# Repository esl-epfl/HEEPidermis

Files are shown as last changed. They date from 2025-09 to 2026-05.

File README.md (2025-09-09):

# Welcome!

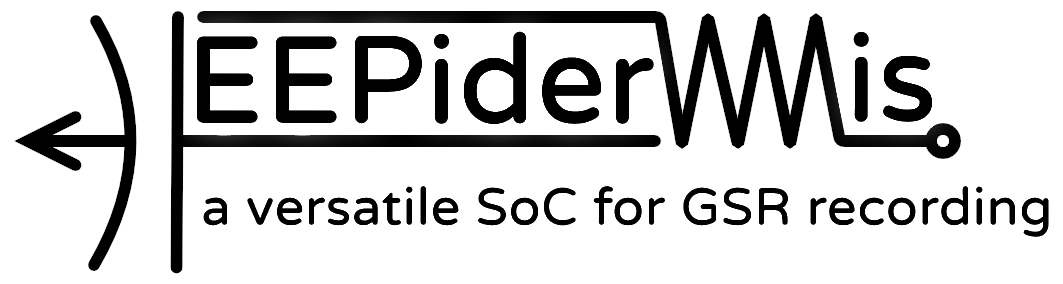
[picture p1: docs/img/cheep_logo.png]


HEEPidermis is a chip based on the open-source RISC-V platform [X-HEEP](https://github.com/esl-epfl/x-heep) intended to record Galvanic Skin Response (GSR) and Impedance (Z).
HEEPidermis is capable of injecting arbitrary-wave currents on the skin with an 8-bit iDAC and measure voltage through a 14-bit VCO-based ADC.
Parameters of the iDAC and ADC can be programmed dynamically using the on-board Ibex CPU. Acquired data can be stored in the 16 kB RAM memory for on-chip processing, compression, and transmission.

HEEPidermis can be interfaced through JTAG for code-debugging, SPI to obtain recordings from memory, or UART.
External ADCs and peripherals can also be commanded via SPI.

The Direct Memory Access (DMA) block allows the chip to operate autonomously without the constant interaction of the CPU. Given proper configuration, the DMA can take care of controlling the current injection profile, read data from the local ADC (or an external one), store data and/or transmit it through SPI.
The DMA can additionally re-direct data to a digital Level Crossing (dLC) block to filter data and reduce the output data rate. The output of the dLC can be stored in memory (along timestamps) or be exposed to be used as feedback loop for the analog front-end, interface with transmission circuits or as input to Spiking Neural Networks.
The dLC block also accepts inputs from analog LC ADCs (instead of the on-chip ADC).

HEEPidermis can also decimate 1-bit ΔΣ-ADCs' output with an integrated CIC filter or, alternatively, with an integrated custom smoothing stage, followed by the dLC block.

Being based on the X-HEEP platform, you can check its documentation on how to program, debug, or understand how it was built. We suggest using the [vendorized X-HEEP's documentation](../../hw/vendor/x-heep/docs/source/index.rst).
For all HEEPidermis-specific documentation, please refer to the documentation below.



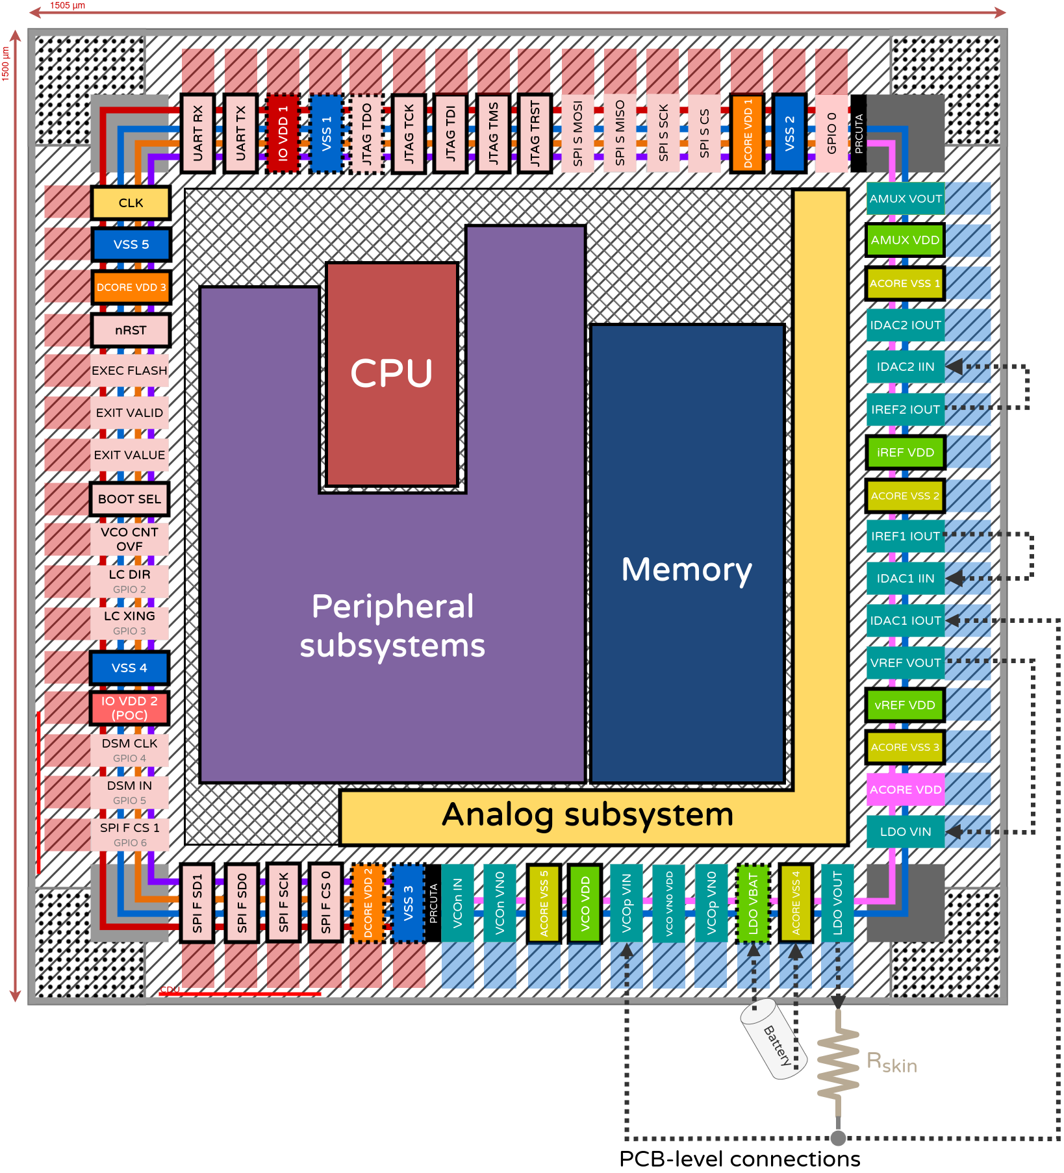
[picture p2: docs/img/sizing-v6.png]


## Index

- **Analog Front End**
  - [Analog subsystem](hw/ip/analog_subsystem/README.md)
  - [iDAC](hw/vendor/analog-library/iDAC/docs/README.md)
  - [VCO](hw/vendor/analog-library/VCO/docs/README.md)

- **Digital Back End**
  - [CPU](./docs/source/DBE/CPU.md)
  - [DMA (how we use it)](./docs/source/DBE/DMA.md)
  - [DMA](hw/vendor/x-heep/docs/source/Peripherals/DMA.md)
  - [SPI host](hw/vendor/x-heep/docs/source/Peripherals/SPI.md)
  - [SPI slave](hw/vendor/x-heep/docs/source/Peripherals/SPI_slave.md)
  - [digital Level-Crossing](hw/vendor/x-heep/docs/source/ExternalPeripherals/dLC.md)
  - [ΔΣ decimation (CIC filter)](./docs/source/DBE/CIC_filter.md)
  - [ΔΣ decimation (SES filter)](./docs/source/DBE/SES_filter.md)

- **Related documents**
  - [HEEPidermis](https://arxiv.org/abs/2509.04528)
  - [ΔΣ Decimation theory](https://ieeexplore.ieee.org/abstract/document/11044062)
  - [iDAC precursor](https://ieeexplore.ieee.org/document/11044212)
  - [VCO Design](https://arxiv.org/abs/2509.06698)

## Prerequisites

Since this project is based on _X-HEEP_, it has the same prerequisites.

1. Follow _X-HEEP_'s [_Prerequisite_](https://github.com/esl-epfl/x-heep/tree/main#prerequisite) section to download the necessary tools.
To correctly generate hardware and software, an extended version of the _core-v-mini-mcu_ environment is required. To install it run:
   ```Bash
   make conda
   ```
Make sure the Conda environment is active:
   ```Bash
   conda activate heepidermis
   ```

2. Make sure that the following tools are available in your system's `PATH`:
   - RISC-V toolchain (supporting at least `rv32imc`)
   - Verible
   - GTKWave
   - Siemens QuestaSim version 2020.4 or above
   - Synopsys Design Compiler version 2020.09 or above
   - Verilator 4

### RTL Simulation

The included [`makefile`](./makefile) proves all the necessary rules to build _HEEPidermis_:

1. Generate all the RTL files (and software headers):
   ```bash
   make cheep-gen
   ```
   Some _X-HEEP_ configuration parameters (e.g. `BUS`, `MEMORY_BANKS` etc.) are still supported, although the default configuration may differ (check [`peripherals_config`](./config/peripherals_config)). In general, these should not be passed through the makefile targets but should be configured in the hjson files in the `config` folder.

2. Build the simulation model:
   ```bash
   make verilator-build     # Verilator
   make questasim-build     # QuestaSim
   ```

3. The software build process is primarily handled by _X-HEEP_, and most of its [example applications](./hw/vendor/x-heep/sw/applications/) will work on _HEEPidermis_ as well. You can choose other `BOOT_MODE`, just be sure to match it with the one used with `make *-build` (by default they use `fore`). `force` will be the faster for simulation.

```bash
make app PROJECT=test_dlc_vco BOOT_MODE=force
```

The combinations of compatible linker and boot modes can be found here:
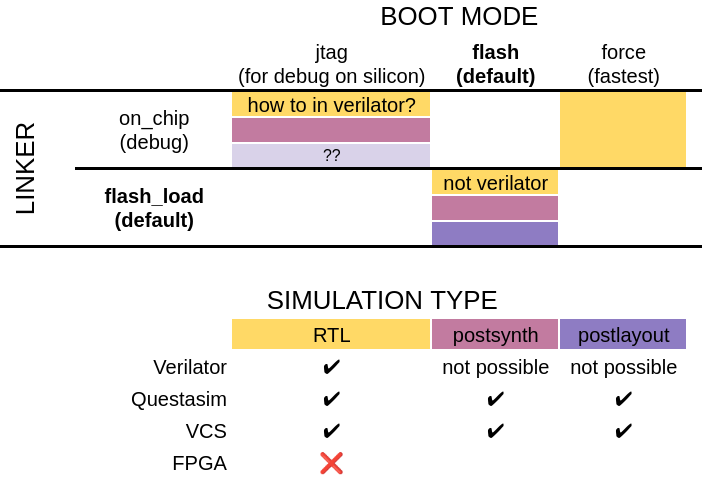
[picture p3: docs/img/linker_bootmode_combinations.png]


1. Launch the simulation with the compiled firmware:
   ```bash
   make verilator-run       # Verilator with waveforms dump
   make verilator-opt       # Verilator without waveforms dump
   make questasim-run       # QuestaSim
   make questasim-gui       # QuestaSim with GUI
   ```

   You can also set other parameters like the `FUSESOC_FLAGS`, `LOG_LEVEL`, `BOOT_MODE`, `VCD_MODE`, etc. to customize the simulation. Refer to the [`makefile`](./makefile) for more details.

2. _HEEPidermis_ `stdout` is exposed through a UART DPI interface at `/dev/pts/<N>`, where `N` is a number printed on the simulation log during execution. You can connect to it using `screen` or similar tools, e.g.:
   ```bash
   screen /dev/pts/0
   ```
   The UART output is also stored to the `uart.log` file in the common simulation directory (`build/sim-common/uart.log`).
   > Using `printf()` will significantly increase the firmware execution time and therefore the simulation. For quick debugging, it recommended to use the return value from `main` instead. When it is _not_ zero, the testbench will print it out at the end of the simulation.

3. The waveforms dumped during the simulation can be opened using:
   ```bash
   make verilator-waves # after Verilator simulation
   make questasim-waves # after QuestaSim simulation
   ```

This will open the waveforms (example from `test_dlc_vco` application):
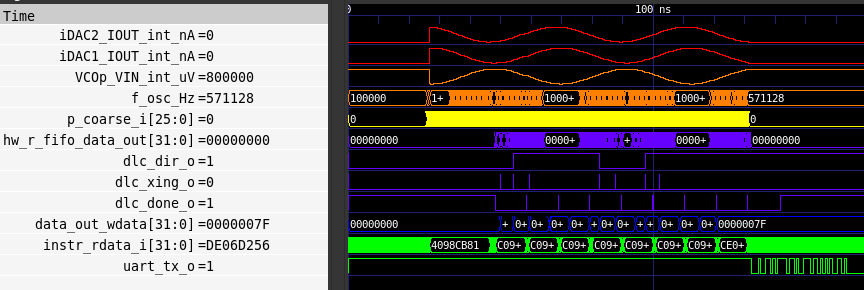
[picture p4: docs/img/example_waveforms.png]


Assuming that your firmware is already available, steps 1., 3., and 4. can be repeated with a single command using the `verilator-sim` or `questasim-sim` targets.

# Questions?

Have questions? curiosities? ideas on how to exploit HEEPidermis? Want to contribute on following versions of the SoC?
Drop an email :) juan.sapriza@epfl.ch

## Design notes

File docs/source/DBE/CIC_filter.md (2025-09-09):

# CIC filter

The CIC filter is implemented as a simplified version of the existing `PDM2PCM` block in the X-HEEP platform. This is achieved by adding a configuration flag, `cic_only`, in the `mcu_cfg.hjson` file. During the `mcu-gen` process, this flag instructs the Python generation scripts to output a reduced SystemVerilog implementation tailored for CIC-only operation, using Mako templates.

For clarity and conciseness, the remainder of this section focuses exclusively on the reduced CIC-only configuration of the block, highlighting the specific modifications made to the original `pdm2pcm` implementation. Additionally, topics shared with the SES filter are covered in greater detail in the corresponding SES section.

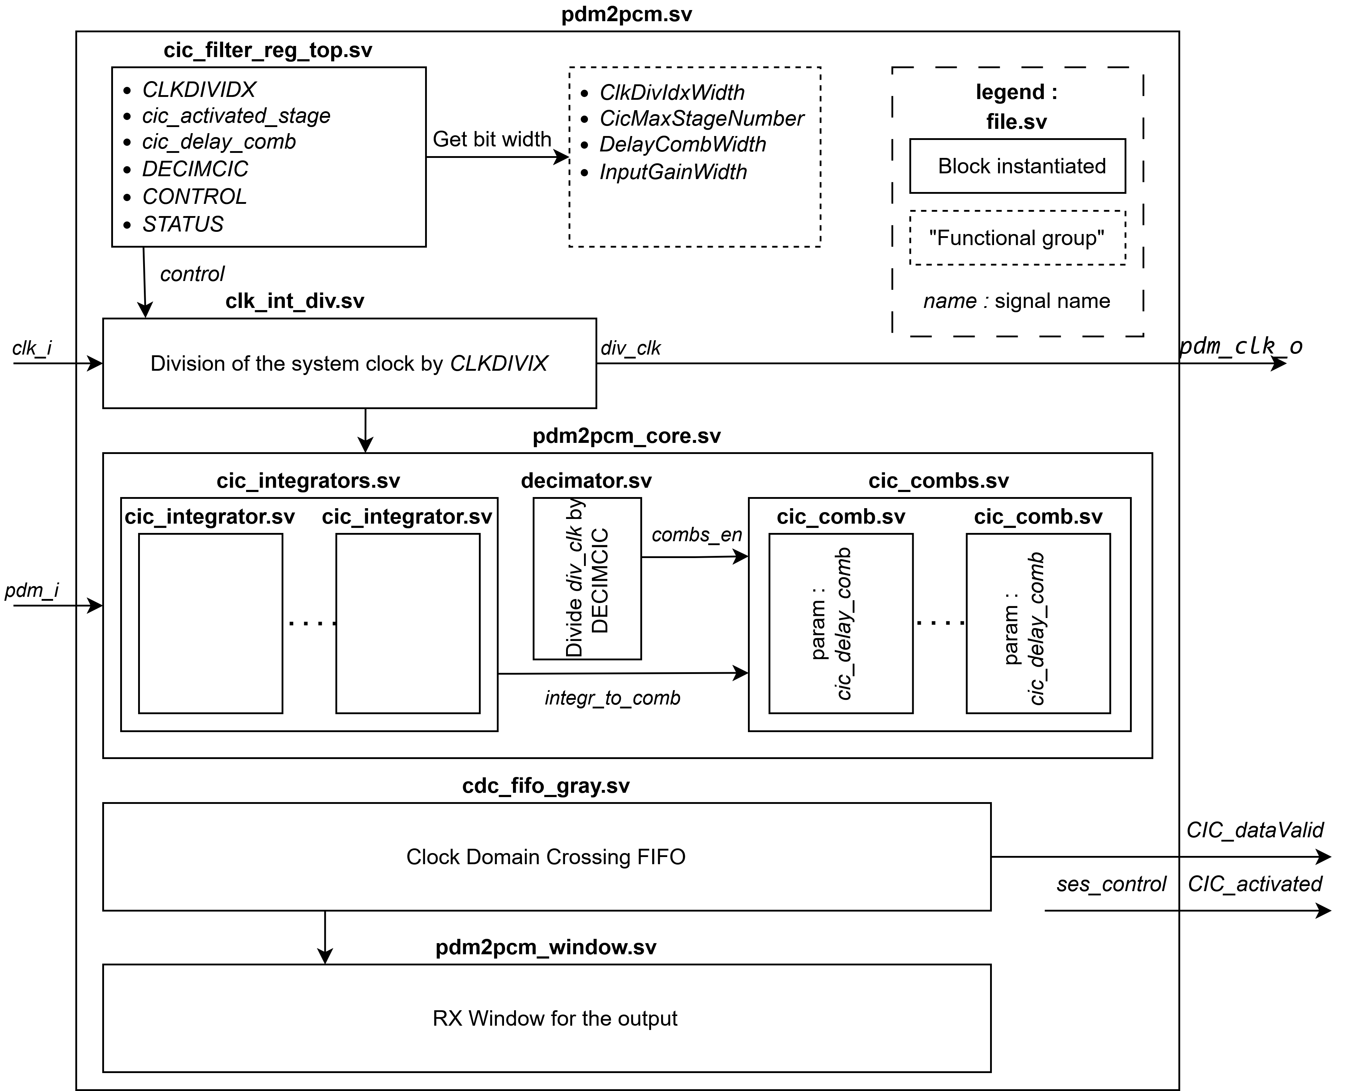
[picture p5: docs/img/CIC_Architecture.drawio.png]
Top level system verilog architecture representation

*Figure: Top level system verilog architecture representation*

## Runtime configurability

This implementation utilizes X-HEEP’s register abstraction to enable seamless communication between C code and SystemVerilog, as detailed in Section SES filter. In the case of the CIC filter, the relevant memory-mapped registers are defined in `pdm2pcm.hjson`.

The following registers are used in the CIC filter configuration:

- **CONTROL** (2 bits): Software control register. The LSB enables or disables the filter; the MSB clears the FIFO buffer.
- **STATUS** (2 bits): Indicates filter status. The LSB signals whether the FIFO is empty, while the MSB indicates if it is full.
- **DECIMCIC** (4 bits): Sets the decimation factor applied between the sampling frequency and the output rate.
- **CLKDIVIDX** (16 bits): Configures the divider between the system clock and the sampling clock.
- **cic_activated_stages** (6 bits): Thermometric, right-aligned bitmask specifying the active CIC stages. The 1s must be contiguous.
- **cic_delay_comb** (4 bits): Defines the delay parameter \( D \) used in the comb stage.
- **RXDATA** (32 bits): Provides access to the filtered output data through a memory-mapped FIFO window.

Detailed information regarding access permissions and bitfield definitions can be found directly in the corresponding `.hjson` configuration file.

## Automatic width adaptation

As for the SES filter, the CIC was updated to allow configuration directly from the width of the register. See more in the corresponding section.

## Integrators and combs

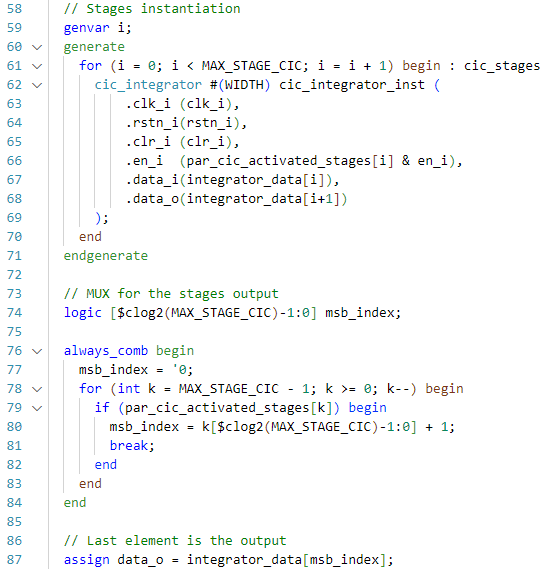
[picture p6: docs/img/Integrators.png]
integrators.sv code snippet, showing the output MUX'ing and the stage generation


*Figure: integrators.sv code snippet, showing the output MUX'ing and the stage generation*

The files `integrators.sv` and `combs.sv` define their respective sections of the CIC filter as parameterized generate blocks. A configurable number of stages is instantiated based on the design parameter `MAX_STAGE_CIC`, with each stage connected in series. This parameter is determined at compile time by checking the width of the `par_cic_activated_stages` register. Stage activation is controlled by the thermometric input `par_cic_activated_stages`, allowing runtime flexibility.

A small combinational logic block scans this activation mask to determine the highest active stage and selects its output for `data_o`. This enables dynamic configuration of the filter depth while maintaining a compact and hardware-efficient implementation.

## Delay D in comb

This block implements a single-stage comb filter, which forms part of the CIC decimation chain. The parameter `par_delay` defines the delay D used in the comb difference equation. Depending on the value of `par_delay`, the filter either bypasses subtraction (when delay is 0) or computes the difference between the current input `data_i` and a delayed version stored in `r_previousdata[par_delay - 1]`.

To support runtime selection of the delay, a shift register of size `MAX_DELAY` stores recent input samples. On each clock cycle (when `en_i` is asserted), the new input is inserted at index 0, and all previous values are shifted forward. This allows the output difference to be computed with any delay value up to `MAX_DELAY`, providing runtime flexibility while maintaining hardware simplicity.

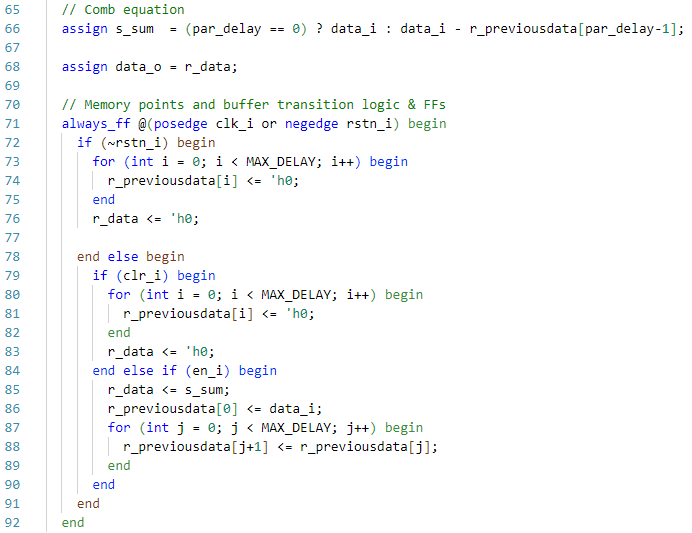
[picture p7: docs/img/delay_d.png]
comb.sv code snippet, showing the usage of the delay parameter

*Figure: comb.sv code snippet, showing the usage of the delay parameter*

## Results

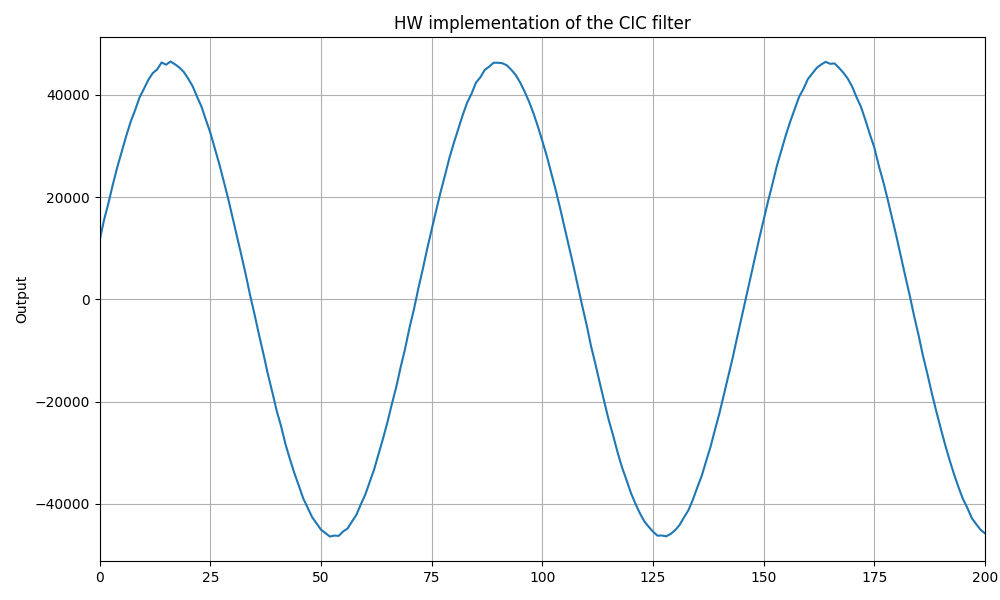
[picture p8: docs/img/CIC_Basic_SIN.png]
Proof of concept, using a perfect sinusoid as input

*Figure: Proof of concept, using a perfect sinusoid as input*

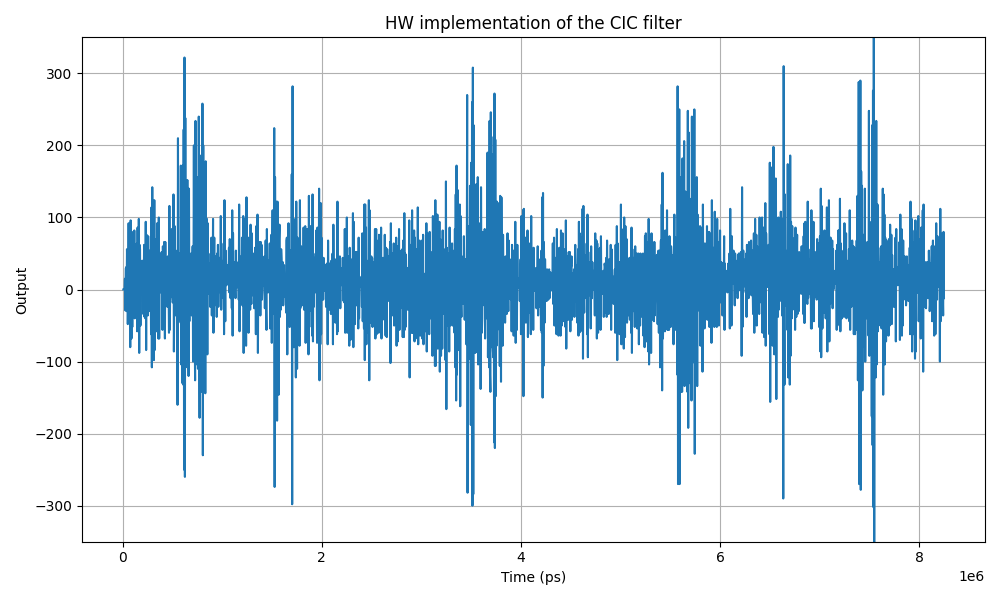
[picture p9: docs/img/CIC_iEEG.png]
Hardware output of the iEEG_10000Hz_85OSR_65dBFS sample file

*Figure: Hardware output of the iEEG_10000Hz_85OSR_65dBFS sample file*

The results obtained for the sinusoidal input closely match the expected ground truth, demonstrating correct filter behavior. Additionally, the output for real EEG signals appears clean and free of significant artifacts. These observations support the successful validation of the project objective.

## Usage

An example of the filter's usage from the software side is provided in the `example_cic` project. This program validates the functionality of the CIC block by comparing its output against predetermined ground truth values.

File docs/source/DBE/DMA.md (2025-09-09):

#  DMA

We have 2 DMA channels. Each DMA channel has an explicit purpose: 

1) For the ADC - to read data from the VCO-ADC decoder
2) For the iDAC - to write data to the iDAC controller

Two DMA channels are needed in order to perform transactions in parallel (injecting current and reading at the same time). 

## The ADC DMA

The ADC DMA should make a reading from the VCO decoder `value` register shortly after the reading value is ready. For this, we have included a dedicated [ADC-timer](./Timers.md) instantiated on the external peripheral subsystem. In SW the timer should be set to the sampling frequency of the ADC. When the timer count has finished it will trigger a refresh signal in the ADC decoder. This will propagate first to the VCO-ADC to get a sample, and few clock cycles later to an `vco_data_ready` signal that is used as a trigger for the DMA through `ext_dma_slot_rx[0]`. This slot enables the DMA to perform one data movement, from the source target (the decoder's `value` register) to a pre-configured destination. 

The ADC DMA is additionally connected to a **streaming accelerator: [the dLC block](./dLC.md)** on the HW-FIFO interface. It can be configured to pass the data through the dLC. This filters the data (decides if and what should be stored) and can proceed to store the resulting value instead of the original one obtained from the VCO-ADC.    

## The DAC DMA

The DAC DMA is used to write into the iDAC registers (primarly the `value` register). To perform this operation at the iDACs refresh-rate, the trigger is controlled by a dedicated [DAC-timer](./Timers.md) also on the external peripheral subsystem. 

## Alternative use: dual-channel VCO + DC current. 

In the case of using DC current, the DAC-DMA will be free, so it could be used to control a second VCO-ADC. 

> ⚠️⚠️⚠️ @ToDo: HOW???!!

## Alternative use: Double-tap operation of the VCO-ADC

If the sampling frequency for the ADC is too slow the counter that keeps track of the number of oscillations will overflow. One alternative to make readings in this case is to do a double-tap: Making a measurement, waiting a short period of time (at some point we had done the math and it was ~300 µs) and perform another reading. 

> ⚠️⚠️⚠️ @ToDo: HOW???!!

## Controlling it from software

The DMAs are completely compatible with the X-HEEP DMA, so please refer to its [documentation](https://x-heep.readthedocs.io/en/latest/Peripherals/DMA.html#) and [examples](https://github.com/esl-epfl/x-heep/tree/main/sw/applications/example_dma) for use cases. 

Below is basic use case configuring the DAC-DMA to write into the iDAC and the ADC-DMA to read the resulting values from the VCO-ADC. 

<details>
<summary>Example code to configure the DMAs</summary>

🎵 Never gonna give you up... 🎶  👀

</details>

## Questions? 

| Topic | Responsible |
|---------------|---------------|
| Mutlichannel | Tommaso Terzano |
| Reconfigurability | Tommaso Terzano |
| HW FIFO | Alessio Naclerio |
| Software | Juan Sapriza, Tommaso Terzano |
| General | Juan Sapriza, Tommaso Terzano, Davide Schiavone |

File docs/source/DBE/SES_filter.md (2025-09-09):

## SES Filter

### Introduction

The filter implemented is a variant of Brown’s Simple Exponential Smoothing (SES) algorithm, adapted for low-power, hardware-efficient delta-sigma post-processing. Originally proposed by Sapriza et al., this SES filter provides a tunable and lightweight alternative to classical CIC filters, supporting runtime reconfiguration with minimal computational overhead.

In the context of *HEEPidermis*, the SES algorithm is expressed using shift-based arithmetic, making it highly suitable for hardware implementation without multipliers. The recursive formulation is as follows:

\[
    \begin{cases}
        \widehat{Y}_i = \widehat{Y}_{i-1} - \widehat{y}_{i-1} + \left(x_i \ll (W_g - 1)\right) \\
        \widehat{y}_i = \widehat{Y}_i \gg W_w
    \end{cases}
\]

Here, $\widehat{Y}_i$ represents the internal state (accumulator), $x_i$ is the 1-bit delta-sigma input scaled by $W_g$, and $W_w$ controls the smoothing strength. This structure enables tunable decimation and filtering with minimal resource usage, making it well-suited for ultra-low-power biomedical applications.

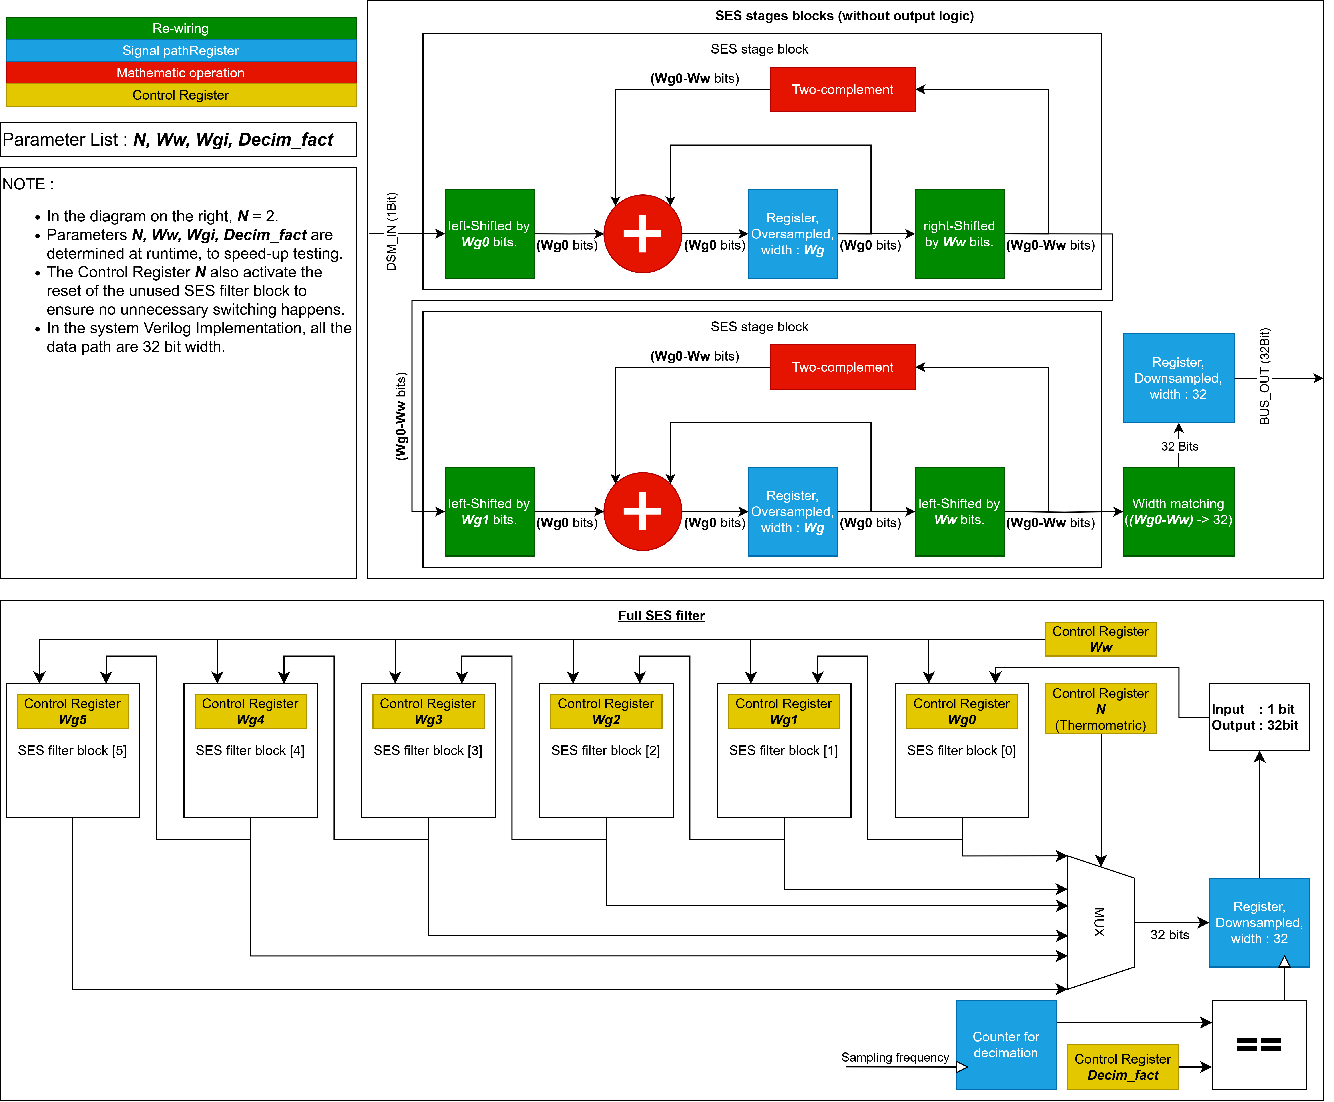
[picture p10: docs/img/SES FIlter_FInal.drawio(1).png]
Schematic representation of the SES filter architecture, showing individual processing stages and the output stage.

*Figure: Schematic representation of the SES filter architecture, showing individual processing stages and the output stage.*

---

### Setup

This setup assumes the installation from the Setup section was executed successfully. The following steps are based mostly on the README from the HEEPidermis GitLab repository.

If everything is set up correctly:

1. Fork the *HEEPidermis* repository to your personal GitLab account and clone it locally.
2. From the root directory of the cloned project, create the required Conda environment.

Once the environment is configured, the complete compilation and simulation flow is:

1. `make cheep-gen` — Generates the configured MCU architecture.
2. `make verilator-build` — Compiles the SystemVerilog sources and builds the simulation model using Verilator.
3. `make app PROJECT=myProject BOOT_MODE=force` — Compiles the C application specified by `myProject`.
4. `make verilator-run BOOT_MODE=force` — Runs the compiled application in the Verilator simulation environment.

---

### Implementation

#### Top level

The system is implemented in a newly created block with a top-level called `ses_filter.sv`. The general "software" architecture with the most important signals is shown below:

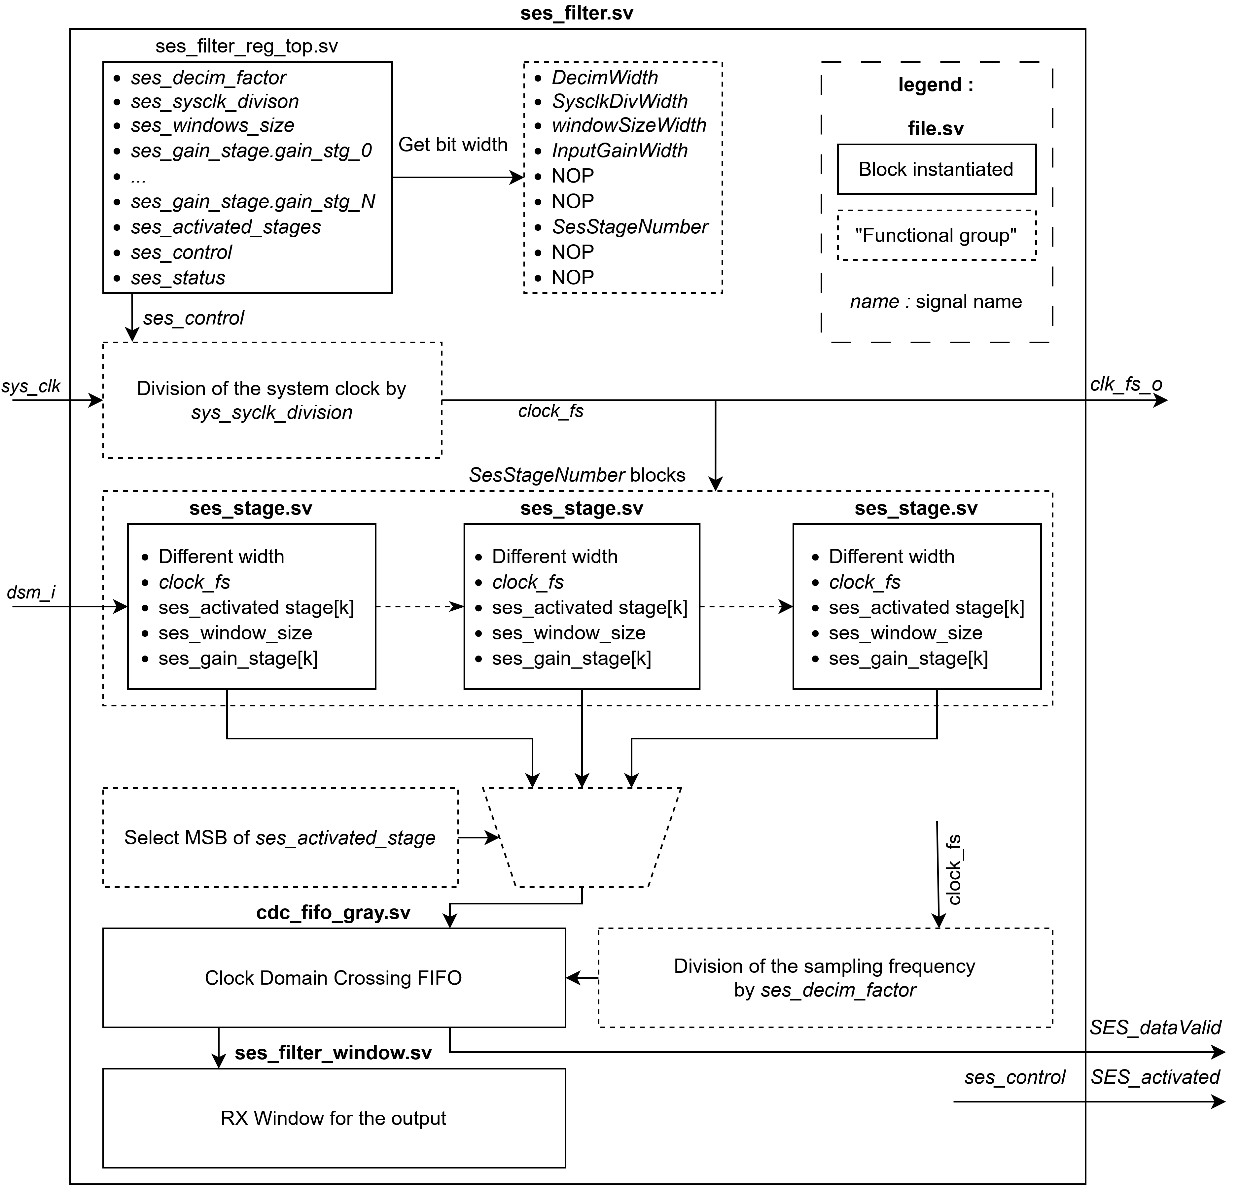
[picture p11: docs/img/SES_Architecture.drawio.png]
Top level system verilog architecture representation

*Figure: Top level system verilog architecture representation*

The design begins by downsampling the system clock to generate a lower-frequency sampling clock, referred to as `clock_fs`. This sampling clock drives the filter pipeline. To safely transfer data back to the system clock domain, a Clock Domain Crossing (CDC) FIFO is used.

A detailed description of the input and output ports is provided in the header comments of the `ses_filter.sv` file.

---

#### Runtime configurability

As for the CIC, this code leverages the X-HEEP/HEEPidermis platform's capability to interface between C code and SystemVerilog through a register abstraction mechanism. The registers are specified in the `ses_filter.hjson` file and generated using the `make cheep-gen` command, which calls the SES_filter.sh script and `regtool.py`.

The following memory-mapped registers are defined:

- **ses_control** (1 bit): Enables or disables the SES filter via software control.
- **ses_status** (2 bits): Provides filter status. LSB: filter active, MSB: new output data available.
- **ses_window_size** (5 bits): Sets the window size parameter \( W_w \) used in the filter computation.
- **ses_decim_factor** (10 bits): Defines the decimation factor applied between the sampling clock and the output rate.
- **ses_sysclk_division** (10 bits): Specifies the division factor from the system clock to the sampling clock.
- **ses_activated_stages** (6 bits): Thermometric, right-aligned bitmask indicating which SES stages are active. The 1s must be contiguous.
- **ses_gain_stages** (30 bits): Encodes the input gain \( W_{g,x} \) for each SES stage (5 bits per stage).
- **rx_data** (32 bits): FIFO window to retrieve filtered output data.

The files `ses_filter_reg_top.sv` and `ses_filter_reg_pkg.sv` are auto-generated and serve as the register interface. See the corresponding `.hjson` file for bitfield definitions.

---

#### Automatic width adaptation

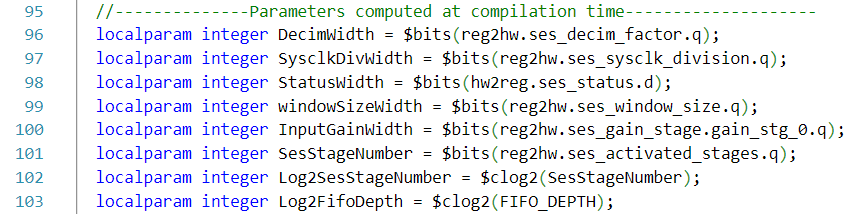
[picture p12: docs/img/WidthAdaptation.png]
ses_filter.sv code snippet, register width extraction

*Figure: ses_filter.sv code snippet, register width extraction*

This design maximizes flexibility by deriving most width-related and structural parameters directly from the register definitions. These values are resolved at compile time, allowing their use in generate blocks and signal width declarations.

For example, the maximum number of SES stages is computed from the width of the corresponding register field. Increasing the maximum number of SES stages only requires adjusting the width of the field and updating the gain configuration in the `.hjson` file. The SystemVerilog code adapts automatically.

The only parameters not derived from register fields are the datapath width (statically 32 bits) and the FIFO depth.

---

#### System clock decimation

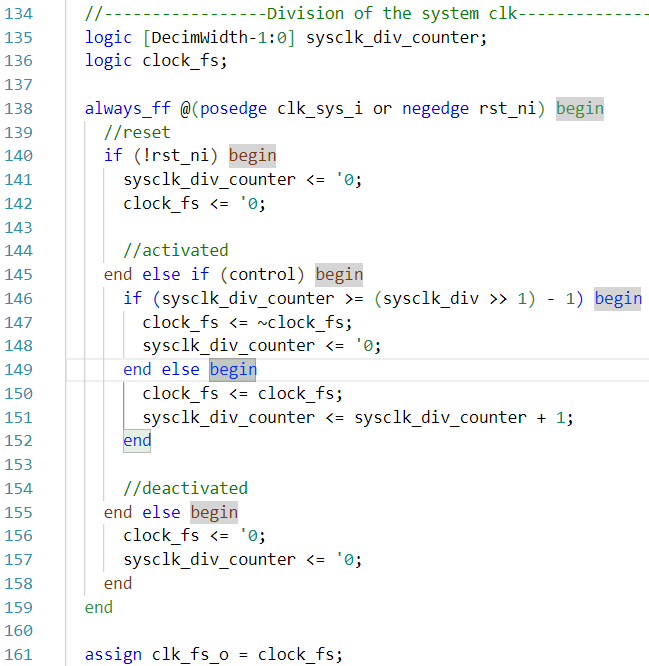
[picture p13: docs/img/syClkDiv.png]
ses_filter.sv code snippet, system clock decimation

*Figure: ses_filter.sv code snippet, system clock decimation*

This block implements a clock divider that generates the sampling clock signal, `clock_fs`, by dividing the main system clock `clk_sys_i` according to the value in `ses_sysclk_division`. The resulting clock `clock_fs` drives the SES filter and is output as `clk_fs_o` to trigger the connected recording device.

The divider logic includes enable and reset handling.

---

#### SES stage generation and internal logic

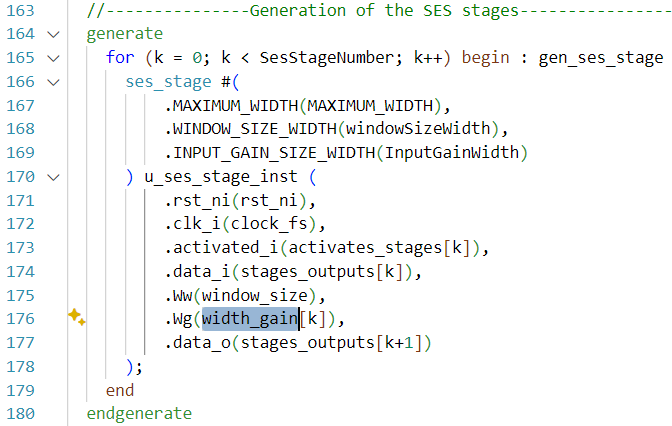
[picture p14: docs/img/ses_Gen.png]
ses_filter.sv code snippet, SES stage generation

*Figure: ses_filter.sv code snippet, SES stage generation*

The generate block instantiates the required number of SES stages based on the parameter derived from the register width. Each `ses_stage` instance is parameterized with maximum data width, window size width, and input gain width. Stages are connected sequentially, with output of stage `k` serving as the input to stage `k+1`. Stage activation and gain configuration are runtime configurable.

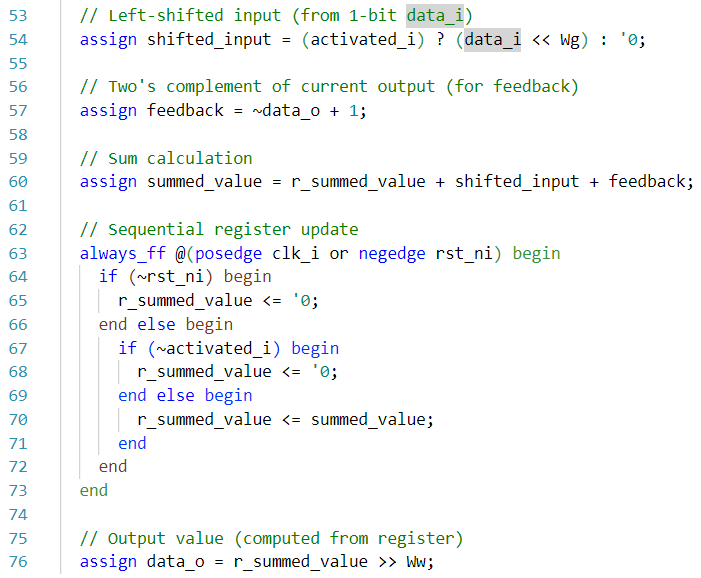
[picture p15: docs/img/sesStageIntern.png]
ses_stage.sv code snippet, internal logic of a single stage

*Figure: ses_stage.sv code snippet, internal logic of a single stage*

The internal logic of a single SES stage implements the mathematical formulation given above. The `activated_i` signal enables complete deactivation for energy-efficient operation.

The input bitstream `data_i` is left-shifted by the gain factor `Wg` when the stage is active. A feedback loop using two's complement implements the accumulator. The sum is stored in `r_summed_value`, reset upon deactivation or global reset. Output `data_o` is obtained by right-shifting the sum by `Ww`.

---

#### Output stage

The final stage is responsible for selecting the correct output, decimating the sampling frequency, and interfacing with the CDC FIFO.

1. **Output Selection (MUX):** The highest active SES stage is selected using a multiplexer.
2. **Decimation Counter:** A counter driven by the sampling clock reduces the output rate by the configured decimation factor.
3. **Clock Domain Crossing (CDC):** A dual-clock FIFO bridges the sampling and system clock domains, delivering data via the memory-mapped interface.
4. **Status Reporting:** A status register combines control state and FIFO validity for software monitoring.

---

## Results

For the following plots, filter parameters were as described in the behavioral model by Juan Sapriza.

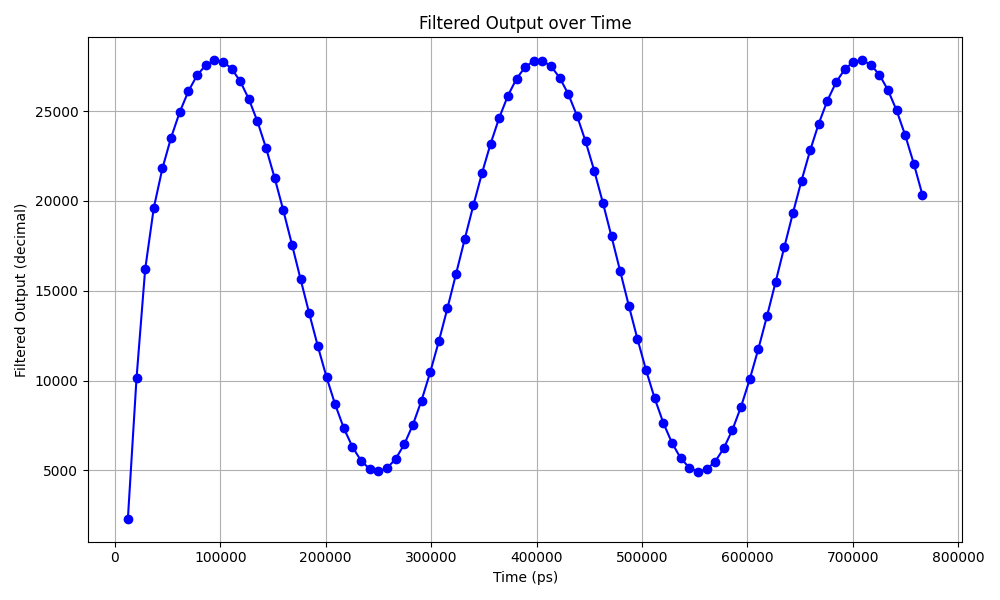
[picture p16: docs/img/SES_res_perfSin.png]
Proof of concept, using a perfect sinusoid as input

*Figure: Proof of concept, using a perfect sinusoid as input*

<div style="display: flex;">
  <div style="flex: 1; margin-right: 10px;">
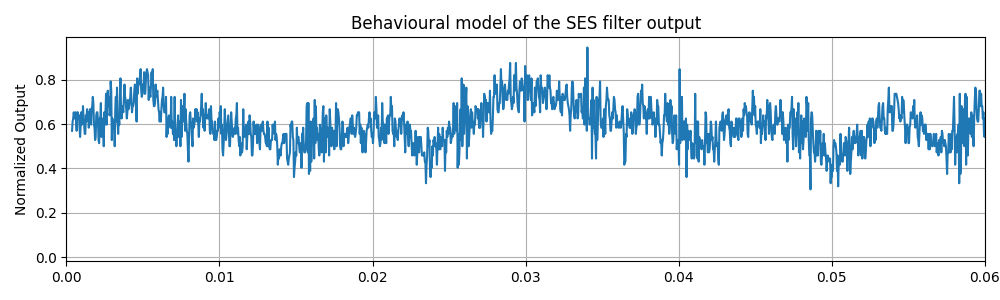
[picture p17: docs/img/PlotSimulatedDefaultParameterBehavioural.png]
Behavioral model output of the iEEG_10000Hz_85OSR_65dBFS sample file
    
    <div style="text-align: center;">Behavioral model output of the iEEG_10000Hz_85OSR_65dBFS sample file</div>
  </div>
  <div style="flex: 1;">
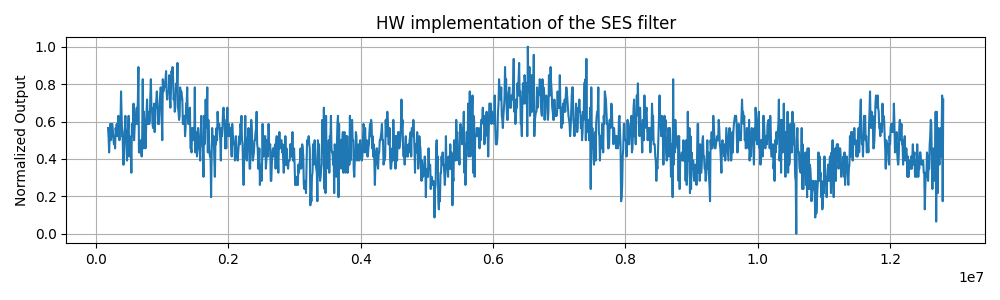
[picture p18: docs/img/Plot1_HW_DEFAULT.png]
Hardware output of the iEEG_10000Hz_85OSR_65dBFS sample file
    
    <div style="text-align: center;">Hardware output of the iEEG_10000Hz_85OSR_65dBFS sample file</div>
  </div>
</div>

<div style="display: flex;">
  <div style="flex: 1; margin-right: 10px;">
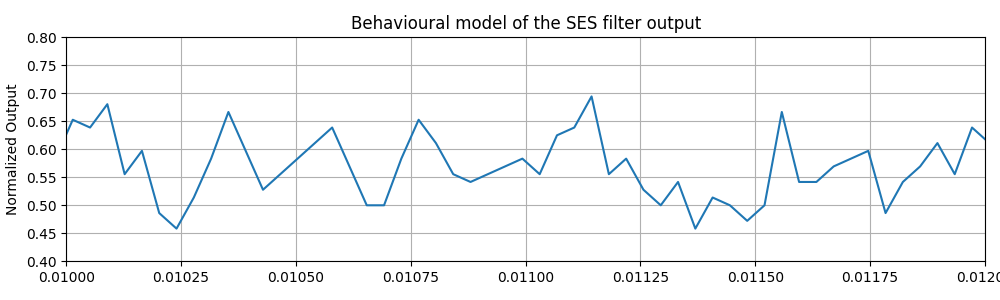
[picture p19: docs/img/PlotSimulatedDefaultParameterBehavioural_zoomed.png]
Behavioral model output (zoomed)
    
    <div style="text-align: center;">Behavioral model output, zoomed</div>
  </div>
  <div style="flex: 1;">
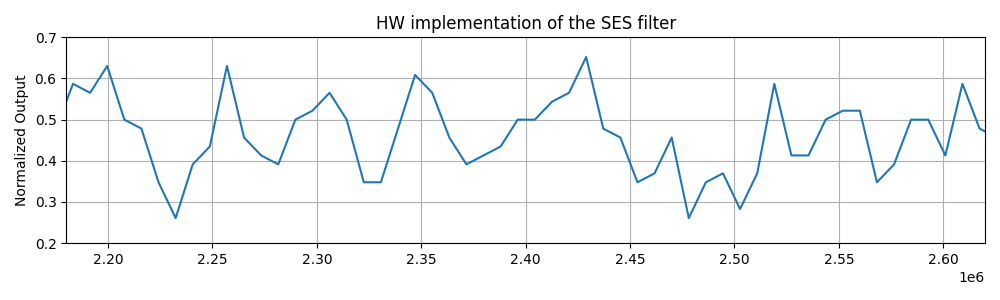
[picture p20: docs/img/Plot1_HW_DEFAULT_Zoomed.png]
Hardware output (zoomed)
    
    <div style="text-align: center;">Hardware output, zoomed</div>
  </div>
</div>

The comparison between the behavioral model and the hardware implementation shows strong agreement. Minor discrepancies are expected due to decimation effects, which result in slightly different input samples being processed. Overall, these results confirm successful validation of the project objective.

Additional graphs below explore the effects of parameter changes on the same input sample. Simulation time is limited to short segments.

<div style="display: flex;">
  <div style="flex: 1; margin-right: 10px;">
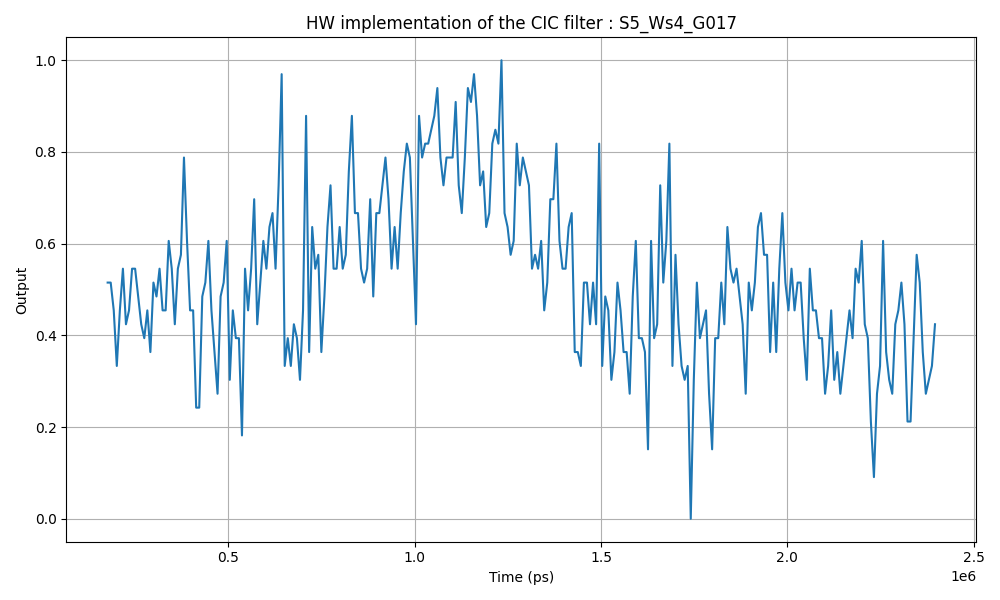
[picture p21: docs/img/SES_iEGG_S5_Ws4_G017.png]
Gain 0: 17, Window: 4, Stages: 5
    
    <div style="text-align: center;">Gain 0: 17, Window: 4, Stages: 5</div>
  </div>
  <div style="flex: 1;">
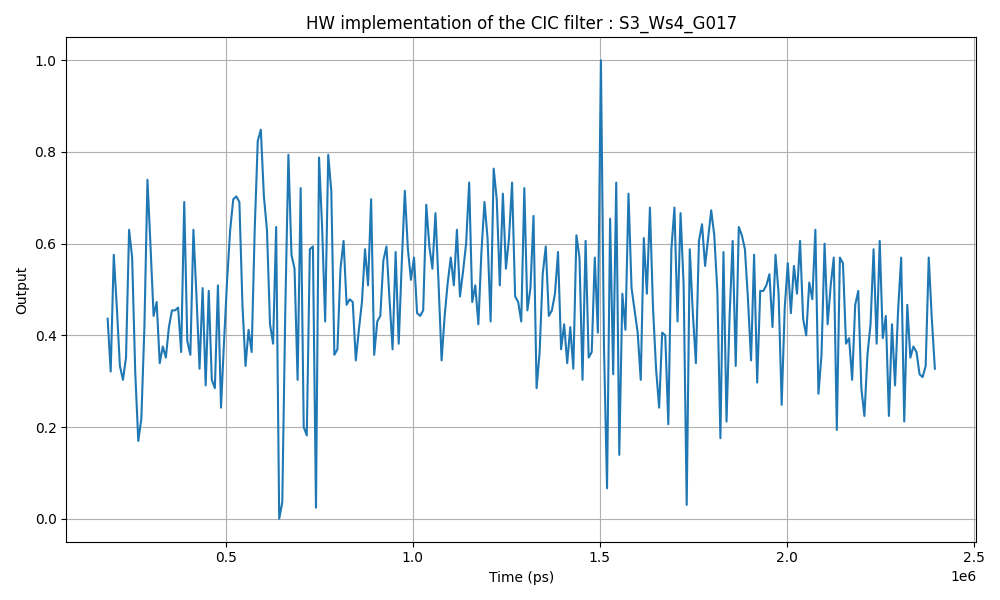
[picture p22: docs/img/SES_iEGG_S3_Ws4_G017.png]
Gain 0: 17, Window: 4, Stages: 3
    
    <div style="text-align: center;">Gain 0: 17, Window: 4, Stages: 3</div>
  </div>
</div>

With the architecture and software-level configurability in place, the next step would be to explore optimal filter configurations. This can now be done directly from software, enabling rapid, automated evaluation.

**NOTE**: The sample file can be found in the behavioral model repository.

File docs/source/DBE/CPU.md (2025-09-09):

#  CPU

HEEPidermis uses the `cv32e20` CPU from OpenHardware Group. 
[Github link](https://github.com/openhwgroup/cve2). 
[Documentation](https://docs.openhwgroup.org/projects/cve2-user-manual/en/latest/)

> This CPU is also known as CVE2, and is a variant of Ibex. 

It is the lowest power variant of the open-source [CORE-V cores](https://github.com/openhwgroup/core-v-cores) 

## About

## Specifications

## Controlling it from software

## Questions? 

| Topic | Responsible |
|---------------|---------------|
| Design | Davide Schiavone |
| Software | Juan Sapriza, David Mallasen |

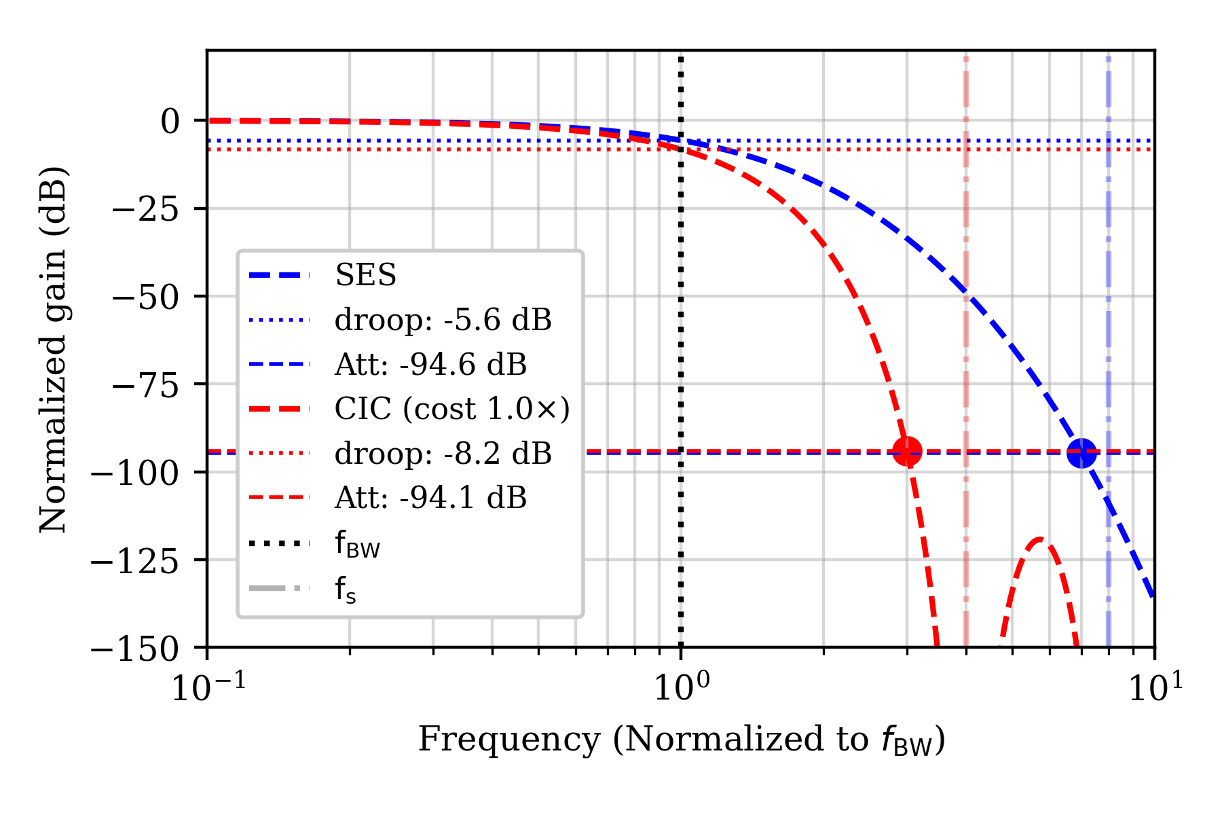
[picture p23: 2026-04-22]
sw/applications/dsm/extdriven_exploration/figs/SES_vs_CIC_H(z)_droop.png

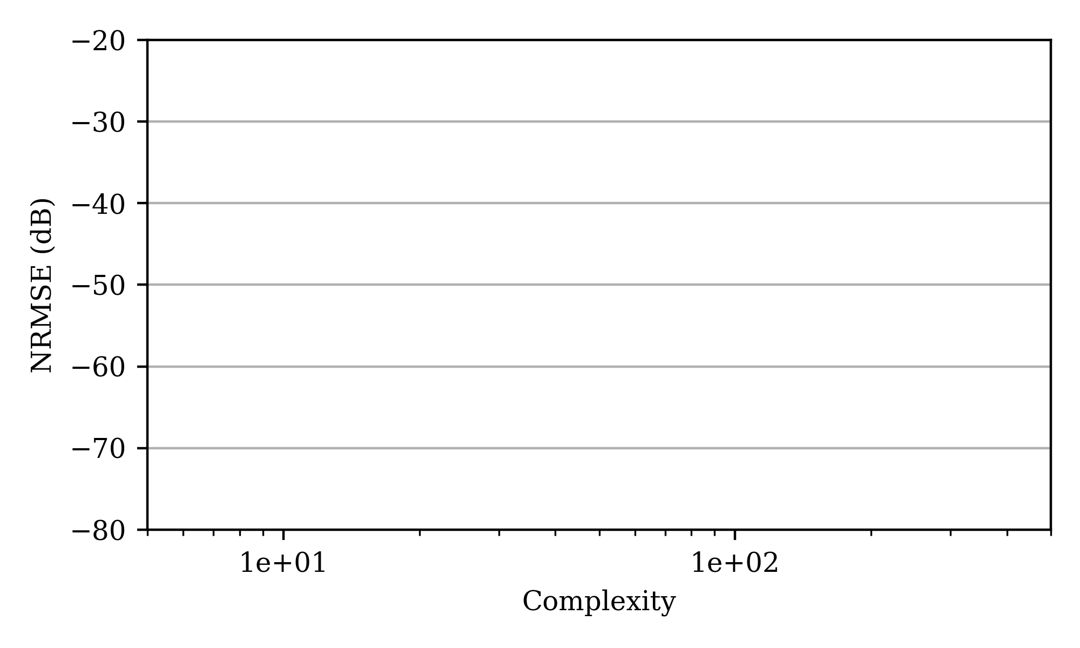
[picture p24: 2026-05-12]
sw/applications/dsm/extdriven_exploration/figs/NRMSE_vs_complexity_CIC_5859Hz_fclk_16MHz.png

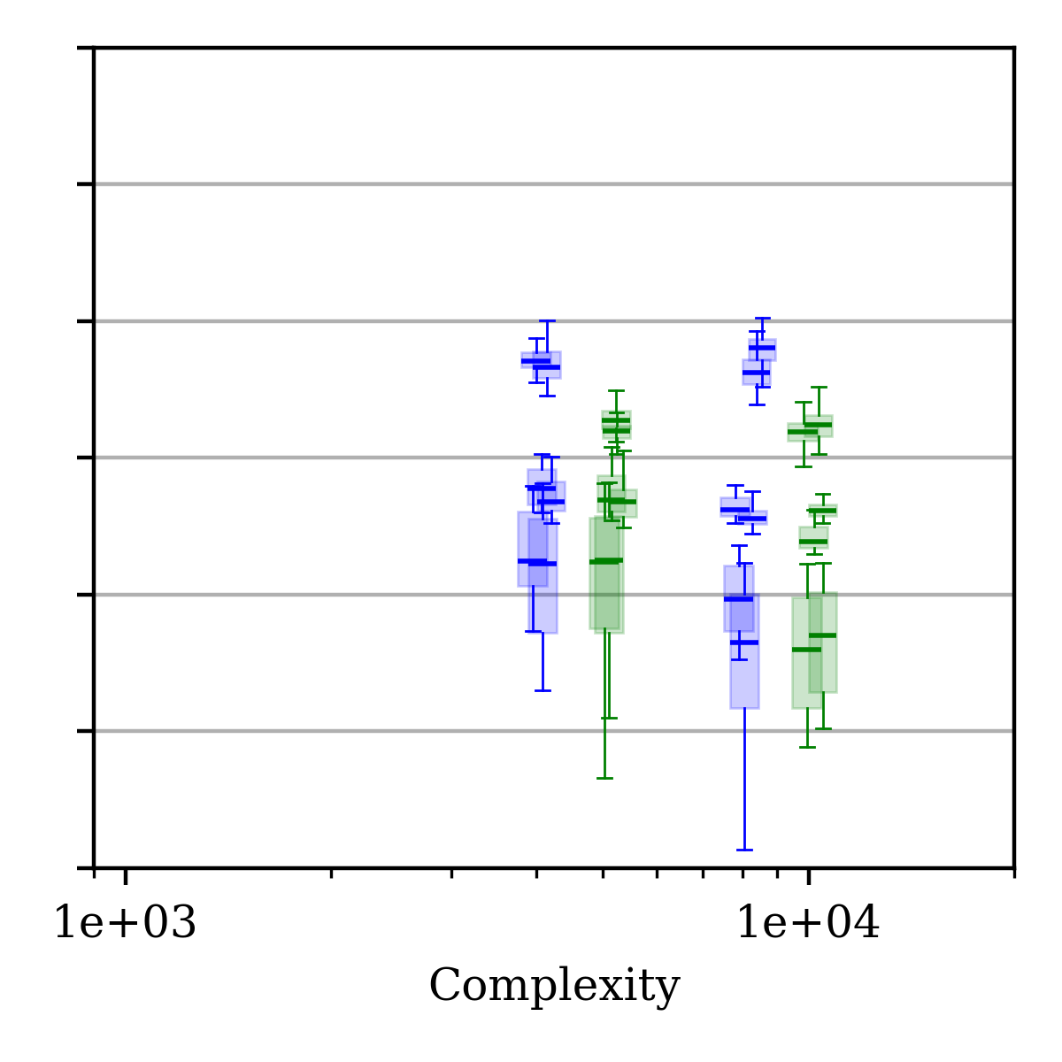
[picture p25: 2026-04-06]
sw/applications/dsm/extdriven_exploration/figs/NRMSE_vs_complexity_SES_976Hz_fclk_8MHz.png

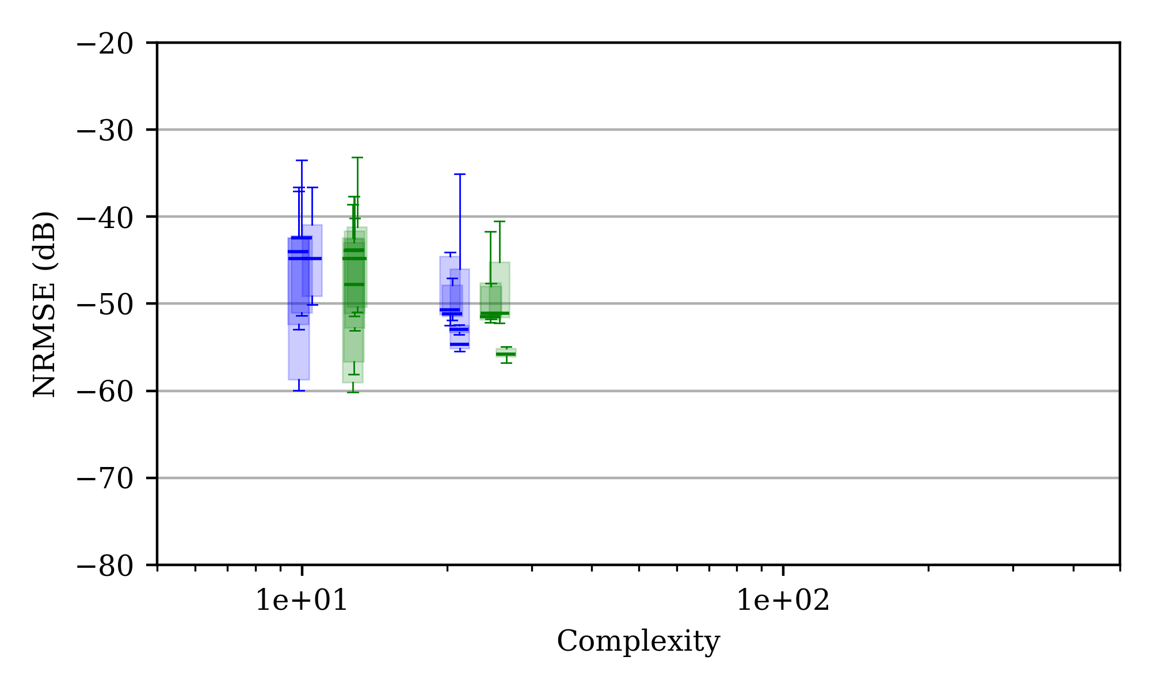
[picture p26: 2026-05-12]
sw/applications/dsm/extdriven_exploration/figs/NRMSE_vs_complexity_SES_146Hz_fclk_16MHz.png

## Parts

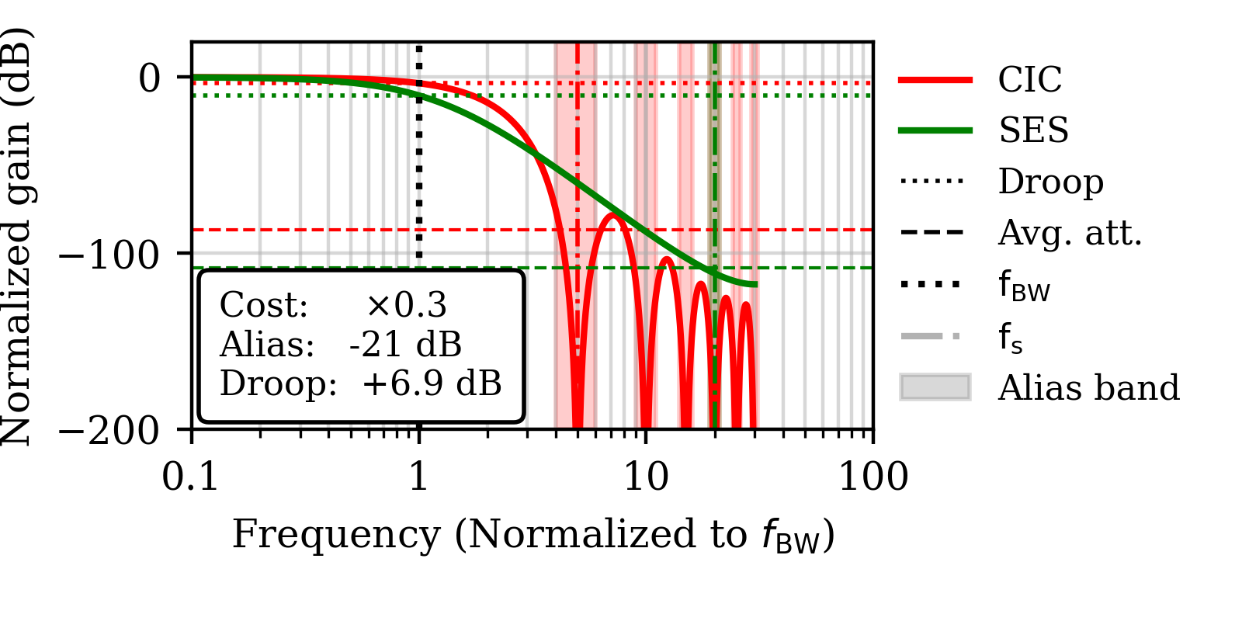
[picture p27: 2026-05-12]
sw/applications/dsm/extdriven_exploration/figs/SES_vs_CIC_H(z)_only_cost.png

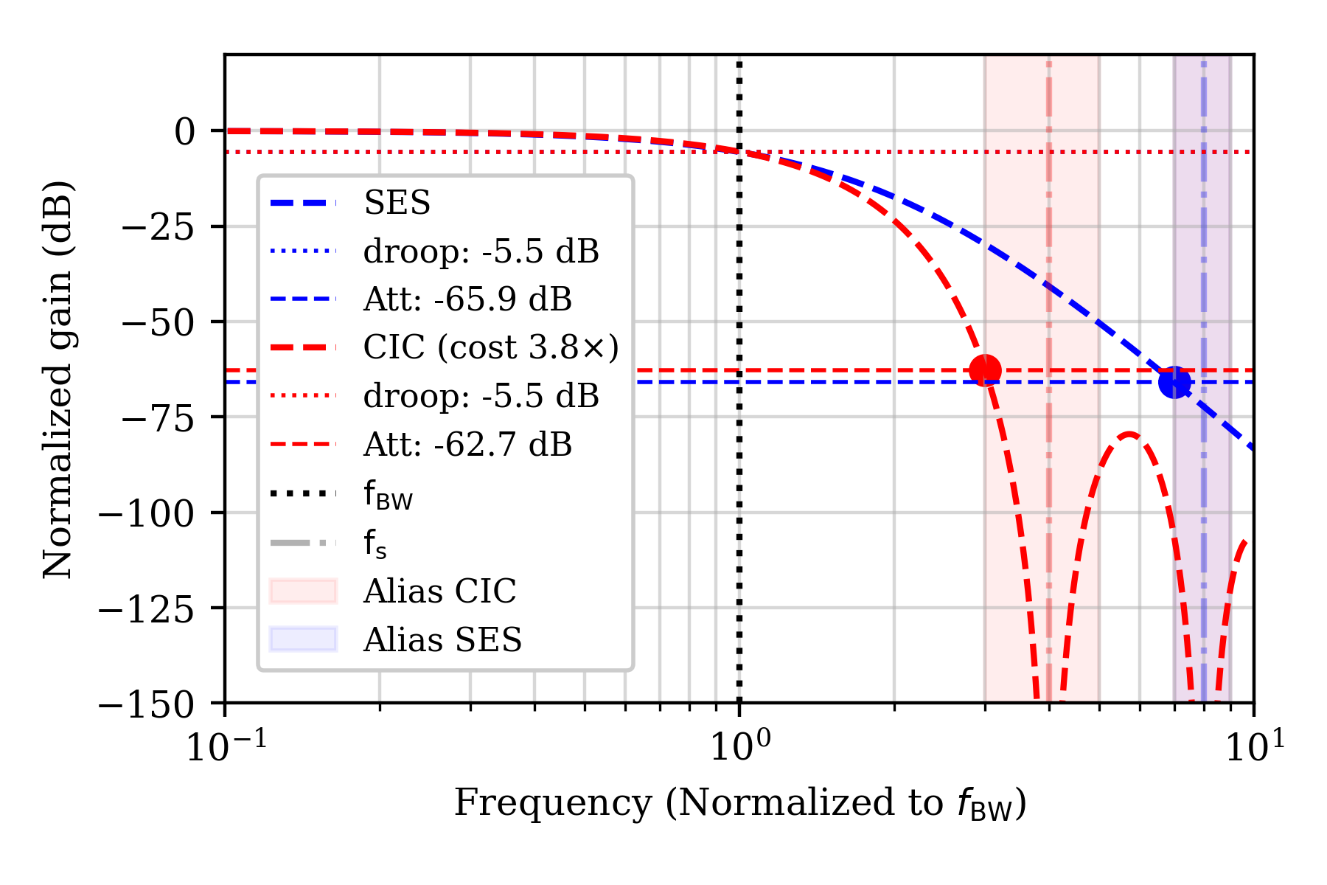
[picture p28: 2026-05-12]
sw/applications/dsm/extdriven_exploration/figs/SES_vs_CIC_H(z)_cost.png

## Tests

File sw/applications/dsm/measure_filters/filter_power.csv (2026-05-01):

Filter | Combs | Wg | Ww | DF | AS | Power (µW)
CIC | 1 |  |  | 200 | 6 | 6.98
CIC | 1 |  |  | 100 | 6 | 9.38
CIC | 1 |  |  | 50 | 6 | 12.85
CIC | 1 |  |  | 50 | 6 | 13.01
CIC | 1 |  |  | 32 | 6 | 29.77
CIC | 1 |  |  | 50 | 6 | 12.96
CIC | 2 |  |  | 50 | 6 | 12.85
CIC | 3 |  |  | 50 | 6 | 13.07
CIC | 3 |  |  | 50 | 5 | 11.23
CIC | 2 |  |  | 50 | 5 | 10.95
CIC | 1 |  |  | 50 | 5 | 11.00
CIC | 1 |  |  | 50 | 4 | 8.99
CIC | 1 |  |  | 50 | 3 | 6.98
CIC | 1 |  |  | 50 | 2 | 5.20
CIC | 1 |  |  | 50 | 1 | 2.96
CIC | 1 |  |  | 32 | 1 | 5.25
CIC | 1 |  |  | 32 | 2 | 10.45
CIC | 1 |  |  | 32 | 3 | 15.30
CIC | 1 |  |  | 32 | 4 | 20.11
CIC | 1 |  |  | 32 | 5 | 25.19
CIC | 1 |  |  | 32 | 6 | 30.16
SES |  | 16 | 4 | 100 | 6 | 2.12
SES |  | 16 | 4 | 100 | 5 | 2.12
SES |  | 16 | 4 | 100 | 4 | 2.12
SES |  | 16 | 4 | 100 | 3 | 2.07
SES |  | 16 | 4 | 100 | 2 | 2.07
SES |  | 16 | 4 | 100 | 1 | 2.07
SES |  | 16 | 4 | 50 | 6 | 2.12
SES |  | 8 | 4 | 50 | 6 | 2.07
SES |  | 16 | 6 | 50 | 6 | 2.35
SES |  | 16 | 8 | 50 | 6 | 3.52
SES |  | 16 | 7 | 50 | 6 | 2.63
SES |  | 16 | 5 | 50 | 6 | 2.18
SES |  | 16 | 3 | 50 | 6 | 2.07
SES |  | 16 | 2 | 50 | 6 | 2.01

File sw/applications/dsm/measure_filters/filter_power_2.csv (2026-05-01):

Filter | Wg | Ww | DF | AS | Power (µW)
CIC |  |  | 200 | 6 | 6.98
CIC |  |  | 100 | 6 | 9.38
CIC |  |  | 50 | 6 | 12.85
CIC |  |  | 50 | 6 | 13.01
CIC |  |  | 32 | 6 | 29.77
CIC |  |  | 50 | 6 | 12.96
CIC |  |  | 50 | 5 | 11.00
CIC |  |  | 50 | 4 | 8.99
CIC |  |  | 50 | 3 | 6.98
CIC |  |  | 50 | 2 | 5.20
CIC |  |  | 50 | 1 | 2.96
CIC |  |  | 32 | 1 | 5.25
CIC |  |  | 32 | 2 | 10.45
CIC |  |  | 32 | 3 | 15.30
CIC |  |  | 32 | 4 | 20.11
CIC |  |  | 32 | 5 | 25.19
CIC |  |  | 32 | 6 | 30.16
SES | 16 | 4 | 100 | 6 | 2.12
SES | 16 | 4 | 100 | 5 | 2.12
SES | 16 | 4 | 100 | 4 | 2.12
SES | 16 | 4 | 100 | 3 | 2.07
SES | 16 | 4 | 100 | 2 | 2.07
SES | 16 | 4 | 100 | 1 | 2.07
SES | 16 | 4 | 50 | 6 | 2.12
SES | 8 | 4 | 50 | 6 | 2.07
SES | 16 | 6 | 50 | 6 | 2.35
SES | 16 | 8 | 50 | 6 | 3.52
SES | 16 | 7 | 50 | 6 | 2.63
SES | 16 | 5 | 50 | 6 | 2.18
SES | 16 | 3 | 50 | 6 | 2.07
SES | 16 | 2 | 50 | 6 | 2.01

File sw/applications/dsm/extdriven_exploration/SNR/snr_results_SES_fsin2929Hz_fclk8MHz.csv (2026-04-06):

FileName | fsin | SNR_dB
SES_fclk_1000_kHz__Wg_16_Ww_3_DF_16_AS_15.csv | 2929.6875 | 62.08484296
SES_fclk_1000_kHz__Wg_16_Ww_3_DF_16_AS_31.csv | 2929.6875 | 67.72129368
SES_fclk_1000_kHz__Wg_16_Ww_3_DF_1_AS_15.csv | 2929.6875 | 0
SES_fclk_1000_kHz__Wg_16_Ww_3_DF_1_AS_31.csv | 2929.6875 | 0
SES_fclk_1000_kHz__Wg_16_Ww_3_DF_32_AS_15.csv | 2929.6875 | 37.06250971
SES_fclk_1000_kHz__Wg_16_Ww_3_DF_32_AS_31.csv | 2929.6875 | 44.08023381
SES_fclk_1000_kHz__Wg_16_Ww_4_DF_16_AS_15.csv | 2929.6875 | 69.50243616
SES_fclk_1000_kHz__Wg_16_Ww_4_DF_16_AS_31.csv | 2929.6875 | 70.90373745
SES_fclk_1000_kHz__Wg_16_Ww_4_DF_1_AS_15.csv | 2929.6875 | 0
SES_fclk_1000_kHz__Wg_16_Ww_4_DF_1_AS_31.csv | 2929.6875 | 0
SES_fclk_1000_kHz__Wg_16_Ww_4_DF_32_AS_15.csv | 2929.6875 | 57.00985993
SES_fclk_1000_kHz__Wg_16_Ww_4_DF_32_AS_31.csv | 2929.6875 | 64.18738386
SES_fclk_1000_kHz__Wg_16_Ww_5_DF_16_AS_15.csv | 2929.6875 | 70.03128885
SES_fclk_1000_kHz__Wg_16_Ww_5_DF_16_AS_31.csv | 2929.6875 | 71.30641848
SES_fclk_1000_kHz__Wg_16_Ww_5_DF_1_AS_15.csv | 2929.6875 | 0
SES_fclk_1000_kHz__Wg_16_Ww_5_DF_1_AS_31.csv | 2929.6875 | 0
SES_fclk_1000_kHz__Wg_16_Ww_5_DF_32_AS_15.csv | 2929.6875 | 68.40267538
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

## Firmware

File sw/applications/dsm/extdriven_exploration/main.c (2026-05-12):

// Copyright EPFL contributors.
// Licensed under the Apache License, Version 2.0, see LICENSE for details.
// SPDX-License-Identifier: Apache-2.0

#include <stdio.h>
#include <stdlib.h>
#include <stdbool.h>
#include "core_v_mini_mcu.h"
#include "gpio.h"
#include "x-heep.h"
#include "soc_ctrl.h"
#include "SES_filter.h"
#include "pdm2pcm_regs.h"


/*
make board_freq PLL_FREQ=8000000
make jtag_open UART_TERMINAL=gnome UART_BAUD=20480
make jtag_build PROJECT=dsm/extdriven_exploration
make jtag_run
*/

// Uncomment to use SES filter. Comment to use CIC filter.
#define SES
#define EAP

#ifdef EAP
  #define SYS_FCLK_HZ 8000000 // 8 MHz needed to coordinate with DSM
  #define DSM_F_S_kHz 1000
  #define DSM_CLK_DIV_CC 8
#else
// LFP mode
  // #define SYS_FCLK_HZ 16000000 // watch out!
  // #define DSM_F_S_kHz 50 //watch out!
  // #define DSM_CLK_DIV_CC 320 // watch out!
// EAP mode for testing
  #define SYS_FCLK_HZ 32000000 // watch out!
  #define DSM_F_S_kHz 1000 //watch out!
  #define DSM_CLK_DIV_CC (SYS_FCLK_HZ/DSM_F_S_kHz*1000) // watch out!
#endif

#define DELAY_BETWEEN_RUNS_cc (SYS_FCLK_HZ*1)
#define RUN_LENGHT_N 1025

#define GPIO_LED 0

#ifdef SES
  #define FILTER_NAME "SES"
#else
  #define FILTER_NAME "CIC"
#endif

#define HEADER(g, w, f, a) printf("\n\n%s\tfclk:%d kHz, Wg:%d,Ww:%d,DF:%d,AS:%d",FILTER_NAME, DSM_F_S_kHz,g,w,f,a );


int main(int argc, char *argv[])
{
    static uint32_t output [RUN_LENGHT_N];
    uint32_t        sample_idx  = 0;
    uint32_t        status, fed, read;
    mmio_region_t   pdm2pcm_base_addr = mmio_region_from_addr((uintptr_t)CIC_START_ADDRESS);

    /* ====================================
    CONFIGURE THE GPIOs
    ==================================== */
    gpio_cfg_t pin_led = { .pin = GPIO_LED, .mode = GpioModeOutPushPull };
    if (gpio_config (pin_led) != GpioOk) {
        printf("GPIO initialization failed!\n");
        return 1;
    }

    #ifdef SES
    //   uint32_t dfs[] = { 1, 16, 32 };       // Decimation factor
    //   uint32_t wgs[] = { 8, 16 };            // Gain of the first stage
    //   uint32_t ass[] = { 15, 31 };           // Mask of activated stages
    //   uint32_t wws[] = { 3, 4, 5 };          // Window lenght (2^x) samples
      uint32_t wgs[] = { 16 };            // Gain of the first stage
      uint32_t dfs[] = { 2, 3, 4, 5, 6};       // Decimation factor
      uint32_t ass[] = { 15, 31, 63 };           // Mask of activated stages
      uint32_t wws[] = { 2, 3, 4 };          // Window lenght (2^x) samples
      #else
      uint32_t dfs[] = { 2, 4, 6, 8, 12, 14, 15 };     // Decimation factor
      uint32_t wgs[] = { DSM_CLK_DIV_CC };   // Clock division (virtual)
      uint32_t ass[] = { 15, 31, 63 };               // Mask of activated stages
      uint32_t wws[] = { 1, 2 }; // Delay comb
    #endif

    uint32_t sim_len_n = sizeof(wgs)*sizeof(ass)*sizeof(wws)*sizeof(dfs)/256;
    uint32_t sim_run;
    // stop the decimation filters
    SES_set_control_reg(0);
    mmio_region_write32(pdm2pcm_base_addr, PDM2PCM_CONTROL_REG_OFFSET, 0);

    SES_set_gain(1, 0);
    SES_set_gain(2, 0);
    SES_set_gain(3, 0);
    SES_set_gain(4, 0);
    SES_set_gain(5, 0);

    printf("\n\n==== Starting loop for %s (%d, %d, %d)====\n\n", FILTER_NAME, SYS_FCLK_HZ, DSM_CLK_DIV_CC, DSM_F_S_kHz);

    printf("\n>>%d",sim_len_n);

    for( uint8_t g=0; g<sizeof(wgs)/4; g++ ){
        for( uint8_t a=0; a<sizeof(ass)/4; a++ ){
            for( uint8_t w=0; w<sizeof(wws)/4; w++ ){
                for( uint8_t f=0; f<sizeof(dfs)/4; f++ ){

                    sim_run = 1+f + w*sizeof(dfs)/4 + a*sizeof(dfs)*sizeof(wws)/16 + g*sizeof(dfs)*sizeof(wws)*sizeof(ass)/64;
                    /* ====================================
                    CONFIGURE THE SES FILTER
                    ==================================== */

                    #ifdef SES
                      SES_set_control_reg(0);                   // stop the decimation filter
                      SES_set_sysclk_division(DSM_CLK_DIV_CC);  // Set the decimator to output a clock at the DSM's sampling frequency
                      SES_set_decim_factor(dfs[f]);             // Set the decimation factor
                      SES_set_activated_stages(ass[a]);         // Set the number of activated stages
                      SES_set_gain(0, wgs[g]);                  // Set gain of the first stage
                      SES_set_window_size(wws[w]);              // Set window size
                    #else
                      mmio_region_write32(pdm2pcm_base_addr, PDM2PCM_CONTROL_REG_OFFSET, 0);                    // stop the decimation filter
                      mmio_region_write32(pdm2pcm_base_addr, PDM2PCM_CLKDIVIDX_REG_OFFSET, wgs[g]);   // Set the decimator to output a clock at the DSM's sampling frequency
                      mmio_region_write32(pdm2pcm_base_addr, PDM2PCM_DECIMCIC_REG_OFFSET, dfs[f]);              // Set the decimation factor
                      mmio_region_write32(pdm2pcm_base_addr, PDM2PCM_CIC_ACTIVATED_STAGES_REG_OFFSET, ass[a]);  // Set the number of activated stages
                      mmio_region_write32(pdm2pcm_base_addr, PDM2PCM_CIC_DELAY_COMB_REG_OFFSET, wws[w]);        // Delay comb
                    #endif

                    // Indicate the start of a recording using a GPIO
                    gpio_write(GPIO_LED, 1);

                    // START the decimation filter
                    #ifdef SES
                      SES_set_control_reg(1); // START the decimation filter
                      do{ status = SES_get_status(); } while (status != 0b11); // Wait for the filter to be ready
                    #else
                      mmio_region_write32(pdm2pcm_base_addr, PDM2PCM_CONTROL_REG_OFFSET, 1);
                      do{ status = mmio_region_read32(pdm2pcm_base_addr, PDM2PCM_STATUS_REG_OFFSET); } while ( status & 1 ); // Not empty
                    #endif

                    /* ====================================
                    ACQUIRE DATA
                    ==================================== */

                    sample_idx = 0;
                    while(1){
                      #ifdef SES
                        if( SES_get_status() == 3 ){
                            output[sample_idx] = SES_get_filtered_output();
                            if(sample_idx++ == RUN_LENGHT_N){
                                SES_set_control_reg(0);
                                break;
                            }
                        }
                      #else
                        status = mmio_region_read32(pdm2pcm_base_addr, PDM2PCM_STATUS_REG_OFFSET);
                        if (!(status & 1)) {
                            output[sample_idx] = mmio_region_read32(pdm2pcm_base_addr, PDM2PCM_RXDATA_REG_OFFSET);
                            if(sample_idx++ == RUN_LENGHT_N){
                              mmio_region_write32(pdm2pcm_base_addr, PDM2PCM_CONTROL_REG_OFFSET, 0);
                              break;
                            }
                        }
                      #endif
                    }

                    if(1){
                        // Indicate the end of a recording using a GPIO
                        gpio_write(GPIO_LED, 0);

                        HEADER(wgs[g], wws[w], dfs[f], ass[a]);
                        for( sample_idx =0; sample_idx < RUN_LENGHT_N; sample_idx++ ){
                        printf("\n%d\t%d", sample_idx, output[sample_idx]);
                        }
                        printf("\n# %d/%d\n", sim_run, sim_len_n);

                        for (int i = 0 ; i < DELAY_BETWEEN_RUNS_cc ; i++) { asm volatile ("nop");}
                    }
                }
            }
        }
    }

    printf("\n\n==== Loop finished ====\n\n");


    return EXIT_SUCCESS;
}

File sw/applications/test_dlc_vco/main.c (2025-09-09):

// Copyright 2024 EPFL and Politecnico di Torino
// Solderpad Hardware License, Version 2.1, see LICENSE.md for details.
// SPDX-License-Identifier: Apache-2.0 WITH SHL-2.1
//
// File: example_dlc_vco/main.c
// Author: Juan Sapriza
// Date: 14/05/2025
// Description: Example application to test the digital Level Crossing (dLC) IP
//              along while the DMA reads from the iDAC.

#include <stdio.h>
#include <stdlib.h>

#include "dma.h"
#include "core_v_mini_mcu.h"
#include "x-heep.h"
#include "cheep.h"
#include "csr.h"
#include "rv_plic.h"

#include "hart.h"
#include "timer_sdk.h"

#include "fast_intr_ctrl.h"

#include "dlc.h"
#include "test_sine.h"
#include "VCO_decoder.h"
#include "iDAC_ctrl.h"

#define PRINTF_IN_SIM 0
#define PRINTF_IN_FPGA 1

#if TARGET_SIM && PRINTF_IN_SIM
        #define PRINTF(fmt, ...)    printf(fmt, ## __VA_ARGS__)
#elif PRINTF_IN_FPGA && !TARGET_SIM
    #define PRINTF(fmt, ...)    printf(fmt, ## __VA_ARGS__)
#else
    #define PRINTF(...)
#endif


#define LC_PARAMS_LC_LSBS_TO_USE_AS_HYSTERESIS 0
#define LC_PARAMS_LC_LEVEL_WIDTH_BY_BITS 7
#define LC_PARAMS_DATA_IN_TWOS_COMPLEMENT 0
#define LC_PARAMS_LC_ACQUISITION_WORD_SIZE_OF_AMPLITUDE 2
#define LC_PARAMS_LC_ACQUISITION_WORD_SIZE_OF_TIME 6
#define LC_PARAMS_LC_LEVEL_WIDTH_BY_FRACTION 256
#define LC_PARAMS_SIZE_PER_SAMPLE_BITS 8
#define LC_STATS_CROSSINGS sizeof(lc_data_for_storage_data)
#define LC_STATS_D_LVL_OVERFLOW_WORDS 49
#define LC_STATS_D_T_OVERFLOW_WORDS 14
#define FORM_STATS_WORD_SIZE_BITS 8

#define INTR_TIMER (1 << 7)
#define INTR_DMA_TRANS_DONE (1 << 19)
#define INTR_DMA_WINDOW_DONE (1 << 30)
#define INTR_EXTERNAL (1<<31)

#define SOURCE_DATA test_sines
#define DATA_LENGTH_B   sizeof(SOURCE_DATA)

#define ADC_DMA 0
#define DAC_DMA 1

dma_target_t adc_tgt_src;
dma_target_t adc_tgt_dst;
dma_trans_t adc_trans;

dma_target_t dac_tgt_src;
dma_target_t dac_tgt_dst;
dma_trans_t dac_trans;

int32_t window_intr_flag = 0;
int32_t transactions_intr_flag = 0;
volatile int32_t xing_intr_flag = 0;

// dLC results buffer
int16_t dlc_results[500];

volatile uint32_t debug __attribute__((section(".xheep_debug_mem")));

void dma_intr_handler_window_done(uint8_t channel){
     if(channel == ADC_DMA ) window_intr_flag ++;
}

void dma_intr_handler_trans_done(uint8_t channel){
    if(channel == ADC_DMA ) transactions_intr_flag ++;
}

void fic_irq_ext_peripheral(){
    xing_intr_flag++;
}

// The DMA transaction validation checks that the window is not too small. If it
// is too small it will assume you are not going to be able to attend the interrupt
// before the next interrupt. Because our interrupts will be very sparse, we override
// this check.
uint8_t dma_window_ratio_warning_threshold(){
    return 0;
}

void __attribute__((aligned(4), interrupt)) handler_irq_timer(void) {
    timer_arm_stop();
    timer_irq_clear();
    return;
}

int main() {

    debug = 'Init';

/*############################################################
################## CONFIGURE THE IDACs ######################*/

    // We enable the two iDACs, each will receive a different signal from the
    // DMA, but will be updated simultaneously.
    iDACs_enable(true, true);
    // Set the calibration values
    iDAC1_calibrate(16);
    iDAC2_calibrate(16);

    // We will be injecting sines with DATA_LENGTH_B/2 samples.
    // The refresh rate we set here will determine the frequency of the sines.
    // Make sure that this is at least double the sampling rate of the ADCs (i dunno, ask Nyquist)
    // Let's say you want 20 ADC samples per period, and that one period has 100 DAC samples,
    // then you want the DAC to be 5 times faster than the ADC, so you set the
    // refresh rate 5 times lower.
    uint16_t dac_refresh_rate_cc = 200;
    iDACs_set_refresh_rate(dac_refresh_rate_cc);
    debug = 'dac';
    debug = (dac_refresh_rate_cc<<16) & 'cc';

/*############################################################
####### CONFIGURE THE iDACs' DMA (1)  ##########################*/

    // Init the DMA (NULL because we will use the internal dma #0)
    // Both DMAs are initialized
    dma_init(NULL);

    // Set the source target (where data is taken from) to the array with the stimulation data
    dac_tgt_src.ptr = (uint8_t*) SOURCE_DATA;

    debug = '1dma';
    debug = dac_tgt_src.ptr;

    // From the memory side there is no restriction on how to fethc data
    dac_tgt_src.trig = DMA_TRIG_MEMORY;
    // These data we will taken from different places in memory, so the increment should be 1 data unit (du)
    dac_tgt_src.inc_d1_du = 1;
    // We will copy data in chunks of 16 bits.
    // Each iDAC takes 8 bits as data, but both their registers are together, with iDAC 0 taking the 8 LSBs and
    // iDAC1 taking the 8 MSBs.
    // Our DMA will take the 16 bit word containing both pieces of data and store them in the common register.
    dac_tgt_src.type = DMA_DATA_TYPE_HALF_WORD;

    // After passing through the dLC, the data will be stored in a separate buffer.
    dac_tgt_dst.ptr = (uint8_t *)(IDAC_CTRL_START_ADDRESS + IDAC_CTRL_CURRENT_REG_OFFSET);
    // Because the data is always stored in the same register, there should be no increment
    dac_tgt_dst.inc_d1_du = 0;
    // Select the appropriate slot -- the iDACs controller is connected to the Tx external trigger
    dac_tgt_dst.trig = DMA_TRIG_SLOT_EXT_TX;
    // We copy the 16-bits containing both iDAC's values
    dac_tgt_dst.type = DMA_DATA_TYPE_HALF_WORD;

    // Set the transaction
    dac_trans.src   = &dac_tgt_src;
    dac_trans.dst   = &dac_tgt_dst;
    // Set that this will be a 1-Dimensional data transfer
    dac_trans.dim   = DMA_DIM_CONF_1D;

    // We will use the DMA channel 1 as th DAC DMA. This could not be in any other way as the
    // transmission interrupts are connected to channel 1's interrupt
    dac_trans.channel = DAC_DMA;

    // No window or transaction end interrupts
    dac_trans.win_du = 0;
    dac_trans.end = DMA_TRANS_END_POLLING;

    // Set the size of the transaction. This should be the size of a period of the signal
    dac_trans.size_d1_du = DATA_LENGTH_B/DMA_DATA_TYPE_2_SIZE(dac_tgt_dst.type);

    // The DMA will restart the same transaction again once it finishes.
    // I will forever be injecting the two sines until it is stopped.
    dac_trans.mode = DMA_TRANS_MODE_CIRCULAR;

    // Specify that we will use the HW FIFO mode: all data read will be forwarded to the
    // stream peripheral that is connected to the hw fifo.
    dac_trans.hw_fifo_en = false;

    debug = 'dma1';

/*############################################################
################## ENABLE DMA INTERRUPTS ######################*/

CSR_SET_BITS(CSR_REG_MSTATUS, 0x8);
CSR_SET_BITS(CSR_REG_MIE, INTR_TIMER | INTR_DMA_TRANS_DONE | INTR_DMA_WINDOW_DONE );
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

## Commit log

2026-01-12 First attempt to use scanf. I think there is a short on HW of the main pcb
2026-04-03 Experiments with DSM
    [CIC_fclk_1000000_kHz__Wg_32_Ww_2_DF_16_AS_63.csv, CIC_fclk_1000000_kHz__Wg_32_Ww_2_DF_1_AS_63.csv, CIC_fclk_1000000_kHz__Wg_32_Ww_2_DF_2_AS_63.csv, CIC_fclk_10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]
2026-04-04 Obtained plots for paper
    [CIC_fclk_1000000_kHz__Wg_32_Ww_2_DF_16_AS_63.csv, CIC_fclk_1000000_kHz__Wg_32_Ww_2_DF_1_AS_63.csv, CIC_fclk_1000000_kHz__Wg_32_Ww_2_DF_2_AS_63.csv, CIC_fclk_10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]
2026-04-06 Added more plots for the SES paper
    [CIC_fclk_50_kHz__Wg_320_Ww_1_DF_16_AS_63.csv, CIC_fclk_50_kHz__Wg_320_Ww_1_DF_1_AS_63.csv, CIC_fclk_50_kHz__Wg_320_Ww_1_DF_2_AS_63.csv, CIC_fclk_50_kHz__Wg_320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]
2026-04-08 Tests on the dLC
    [SES_fclk_1000_kHz__Wg_16_Ww_3_DF_16_AS_15.csv, SES_fclk_1000_kHz__Wg_16_Ww_3_DF_16_AS_31.csv, SES_fclk_1000_kHz__Wg_16_Ww_3_DF_1_AS_15.csv, SES_fclk_1000_kHz__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]
2026-04-13 Added better extraction from dLC + better reconstruction
    [test12.csv, test13.csv, test14.csv, test15.csv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]
2026-05-01 Added power measurement plots
    [filter_power.csv, filter_power_2.csv]
2026-05-12 Measured more CIC/SES power consumptions
    [CIC_fclk_1000_kHz__Wg_16_Ww_1_DF_100_AS_63.csv, CIC_fclk_1000_kHz__Wg_16_Ww_1_DF_14_AS_63.csv, CIC_fclk_1000_kHz__Wg_16_Ww_1_DF_15_AS_63.csv, CIC_fclk_1000_kHz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]
2026-05-27 ⚖ Automatic range adjustment (#10)
